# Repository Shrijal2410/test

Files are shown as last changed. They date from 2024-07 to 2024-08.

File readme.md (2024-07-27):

# Bionic Arm

Our project aims to provide a realistic, functional prosthetic hand for those who have lost theirs. We're not delving into mastering neurology; instead, we're focusing on using muscle sensor data (EMG) to control the hand's movements. Our design is intended for individuals with sufficient remaining limb functionality to provide us with EMG signals, allowing us to move the fingers and wrist accordingly.

## Objectives

Simple enough to outline, but challenging to achieve:

- Create a functional hand with full control over five fingers and wrist movement.
- Ensure the hand can carry up to 1-2kg and grip objects easily.
- Keep the overall weight under 500g, which is a challenge compared to some existing industrial designs.

## Folder Structure

I’ve kept a minimal yet comprehensive folder structure. Ensure each folder has a `README.md`. No spaces in file names use hyphens '-' or underscores '_'. Keep all file and folder names in lowercase. Stick to this template, but feel free to make necessary adjustments.

```
📁 bionicarm
│
├── 🗃️ code
│   └── 🗂️ esp32
│       ├── 🗂️ build
│       │   ├── 🗂️ multipleMotor
│       │   ├── 🗂️ multipleMotorWithGUI
│       │   └── 🗂️ singleMotor
│       └── 🗂️ test
│           ├── 🗂️ pid
│           └── 🗂️ sensorData
│   └── 🗂️ matlab
│
├── 🗃️ data
│   └── 🗂️ raw
│
├── 🗃️ docs
│   └── 🗂️ research
│
├── 🗃️ electrical
│   ├── 🗂️ assets
│   │   ├── 🗂️ 3dmodel
│   │   ├── 🗂️ footprint
│   │   └── 🗂️ symbol
│   ├── 🗂️ production
│   └── 🗂️ schematic
│
└── 🗃️ mechanical
    └── 🗂️ stl
```

## Commit Message Guidelines

Keep commit messages clean and meaningful. Use the following structure and ensure messages are in lowercase:

```
<type>(<scope>): <short summary>
│       │             │
│       │             └─⫸ Summary in present tense. Not capitalized. No period at the end.
│       │                  - use bullet points for clarity
│       │
│       └─⫸ Commit Scope: mechanical|electrical|firmware|software|integration|documentation
│
└─⫸ Commit Type: build|ci|docs|feat|fix|perf|refactor|test
```

### Example

```
feat(firmware-control): add PID controller for motor speed regulation

- enhances motor speed accuracy
- improves response time
```

### Important Note

Stick to this format to avoid the need for commit message modification via `git rebase`, which could inadvertently list me as a contributor to your commit. This ensures proper credit for your work.

## License

Not my area of expertise. So, I’m leaving this part to someone else.

**Note:** The goal of this README is to provide an overview of the project and guide users on where to go. Keep its purpose in mind while updating.

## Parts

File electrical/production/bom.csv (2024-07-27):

Designator | Footprint | Quantity | Value | LCSC Part #
C1, C2, C3 | CP_Radial_D4.0mm_P2.00mm | 3 | C_Small
D1 | D_DO-35_SOD27_P7.62mm_Horizontal | 1 | D_Small
D2, D3 | LED_D5.0mm_Horizontal_O1.27mm_Z3.0mm | 2 | LED_Small
D4 | LED_D5.0mm-4_RGB | 1 | LED_RGBA
F1 | RGEF500 | 1 | Polyfuse_Small
J1 | TerminalBlock_Phoenix_MKDS-1,5-4-5.08_1x04_P5.08mm_Horizontal | 1 | Screw_Terminal_01x04
M1, M2, M3, M4, M5, M6, M7 | JST_1x06_P2.54mm_Vertical | 7 | N20
MD1, MD2, MD3, MD4 | TB6612 | 4 | TB6612
R1, R2, R3, R4 | R_Axial_DIN0207_L6.3mm_D2.5mm_P7.62mm_Horizontal | 4 | R_Small
RV1 | Potentiometer_Runtron_RM-065_Vertical | 1 | R_Potentiometer_Small
S1, S2 | JST_1x03_P2.54mm_Vertical | 2 | EMG2
T1 | TestPoint_Pad_1.0x1.0mm | 1 | TestPoint_Probe
U1 | ESP32 | 1 | ESP32
U2 | SAMD09 | 1 | SAMD09
U3, U4 | CD4069 | 2 | CD4069
U5 | PinHeader_1x03_P2.54mm_Vertical | 1 | LM338

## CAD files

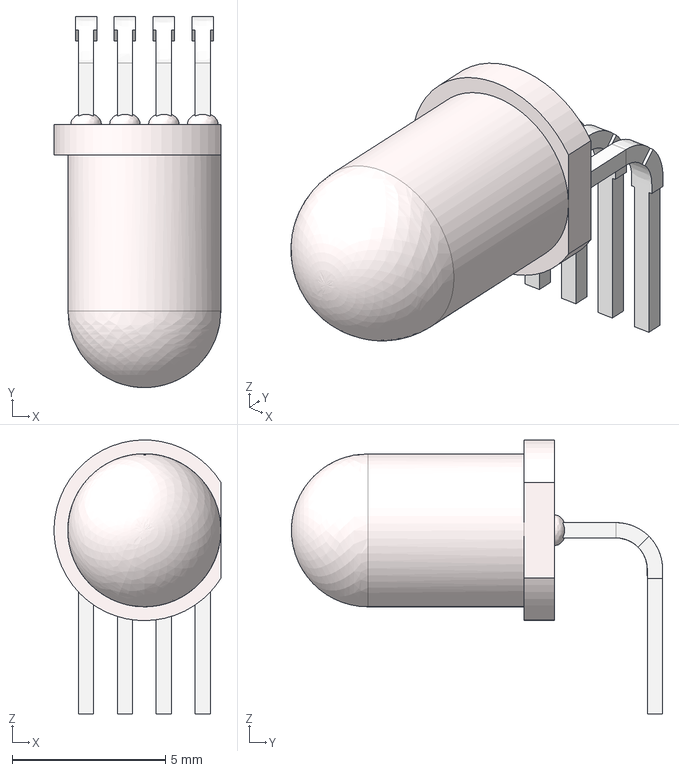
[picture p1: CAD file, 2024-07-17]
electrical/assets/3dmodel/LED_RGB_H1mm.stp
5.45 x 12.1 x 8.95 mm

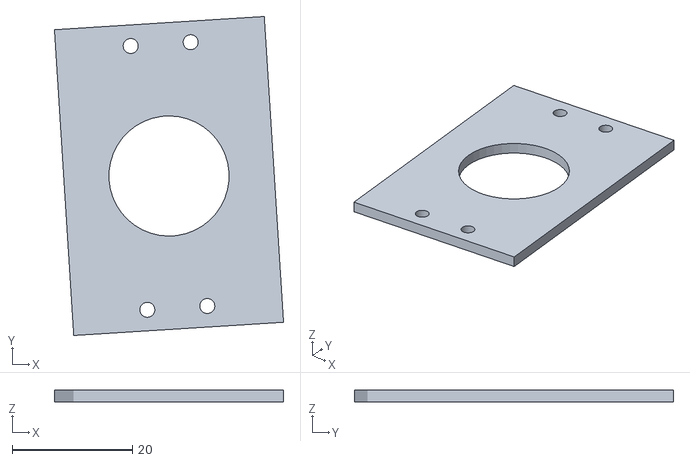
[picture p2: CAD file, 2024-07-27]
mechanical/stl/forearm/Assem2 - Part21-1.STL
38.1 x 53.1 x 2.00

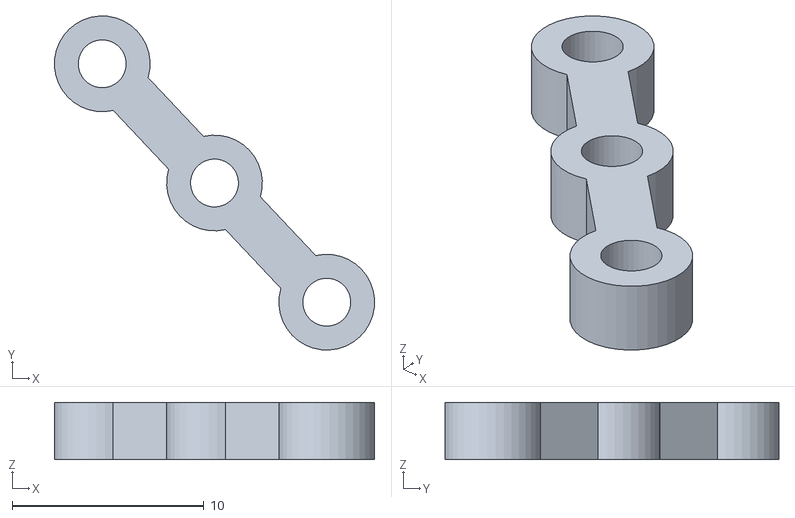
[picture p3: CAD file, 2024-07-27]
mechanical/stl/plam/Assem3 - Part4_middle-1.STL
16.7 x 17.4 x 3.00

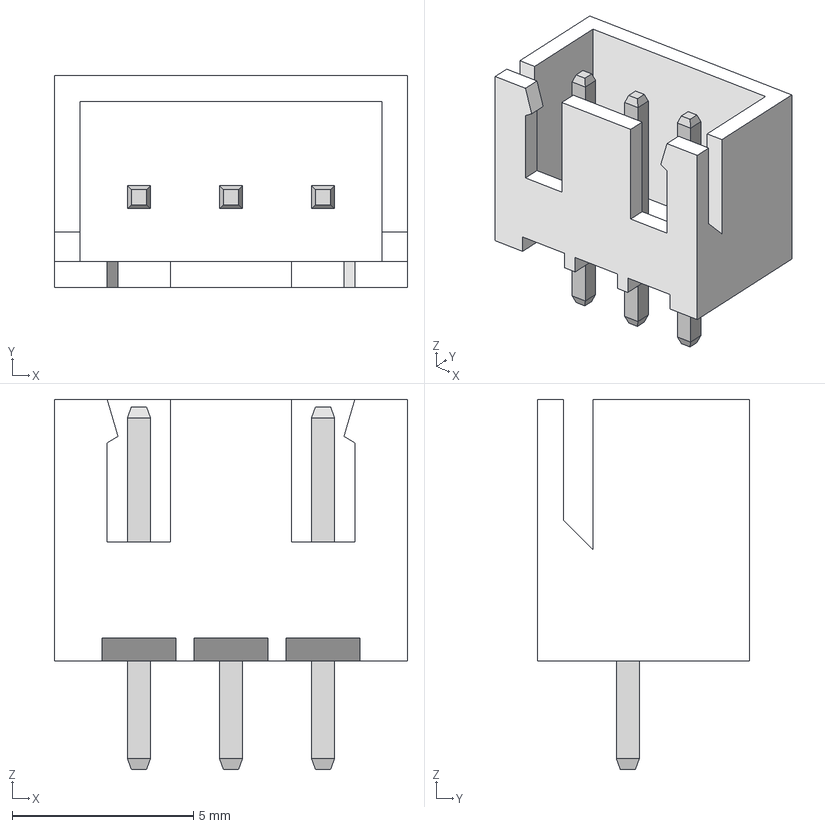
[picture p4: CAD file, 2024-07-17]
electrical/assets/3dmodel/JST_XH_1x03_P2.54mm_Vertical.step
9.75 x 5.84 x 10.2 mm

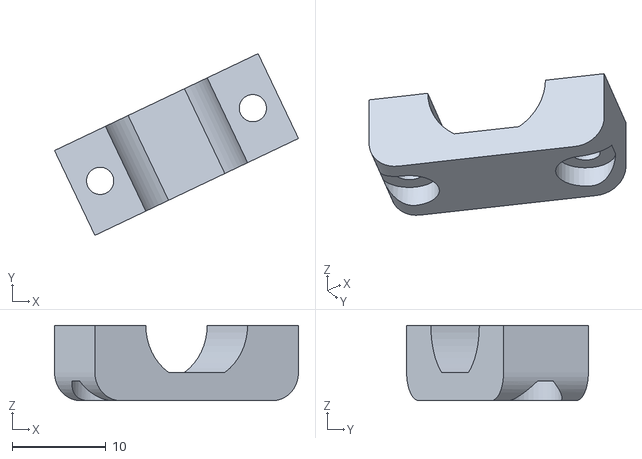
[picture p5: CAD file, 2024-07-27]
mechanical/stl/forearm/Assem2 - Part19-2.STL
26.0 x 19.3 x 8.00

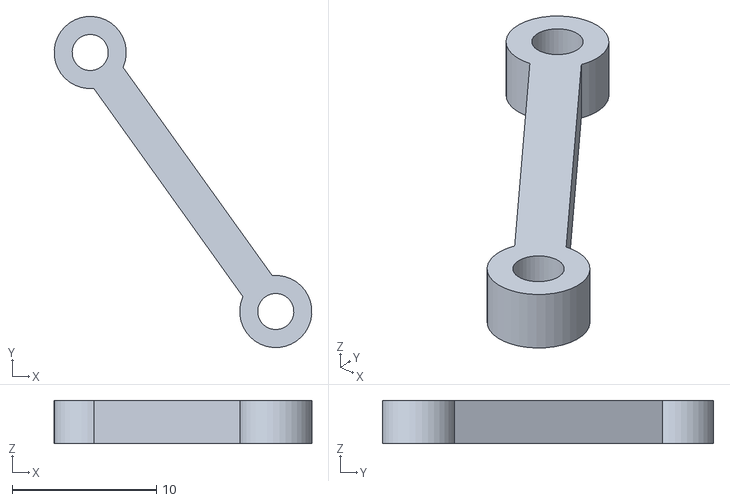
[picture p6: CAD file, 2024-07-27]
mechanical/stl/plam/Assem3 - Part5_little-1.STL
17.8 x 22.9 x 3.00

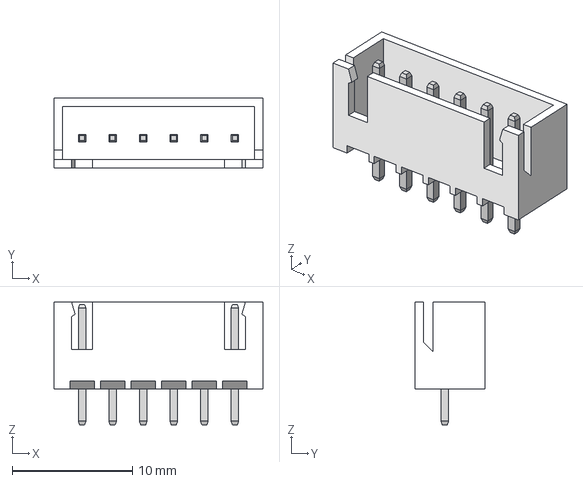
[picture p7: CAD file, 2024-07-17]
electrical/assets/3dmodel/JST_XH_1x06_P2.54mm_Vertical.stp
17.4 x 5.84 x 10.2 mm

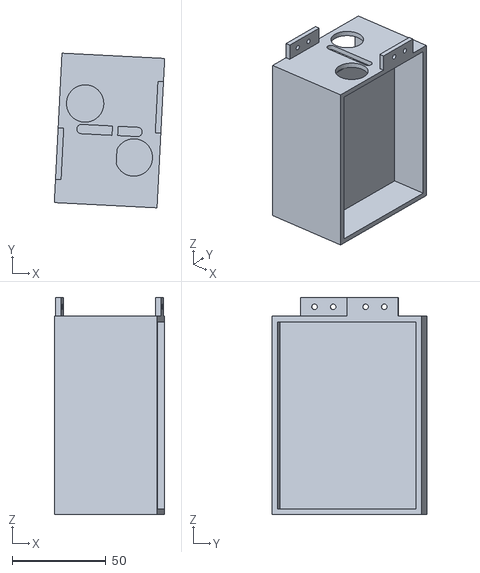
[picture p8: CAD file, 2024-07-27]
mechanical/stl/forearm/Assem2 - Part23-1.STL
59.0 x 82.7 x 116.0

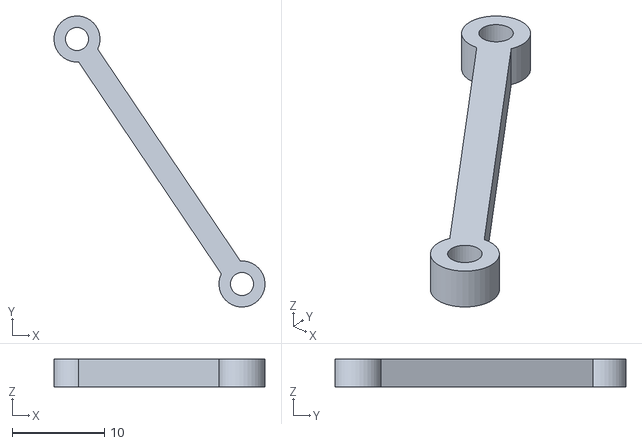
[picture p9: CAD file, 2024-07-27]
mechanical/stl/plam/Assem3 - Part5_thumb-1.STL
22.9 x 31.6 x 3.00

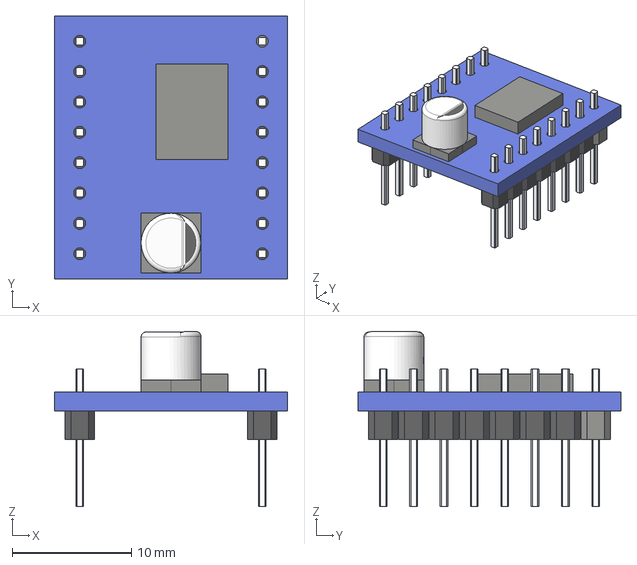
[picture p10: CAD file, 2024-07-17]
electrical/assets/3dmodel/TB6612.step
19.5 x 22.0 x 14.7 mm

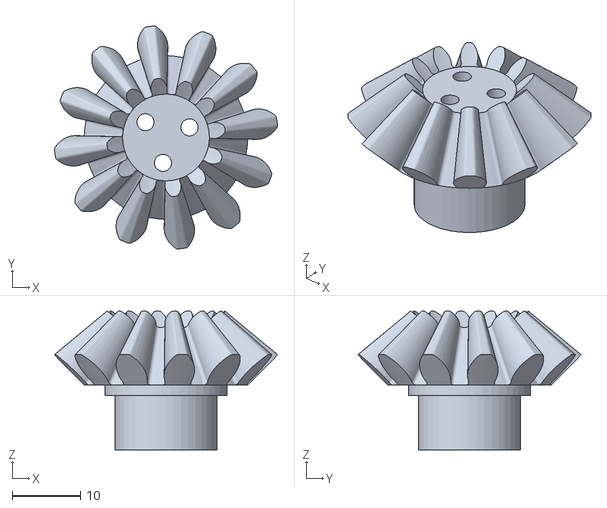
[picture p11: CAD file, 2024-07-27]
mechanical/stl/forearm/Assem2 - Bevel Gear3-3.STL
32.7 x 32.7 x 20.3

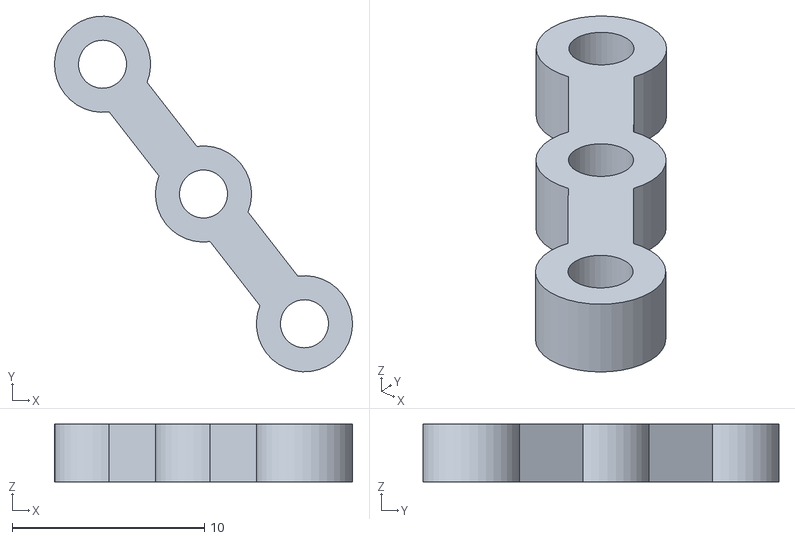
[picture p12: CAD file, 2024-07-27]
mechanical/stl/plam/Assem3 - Part4_little-1.STL
15.5 x 18.5 x 3.00

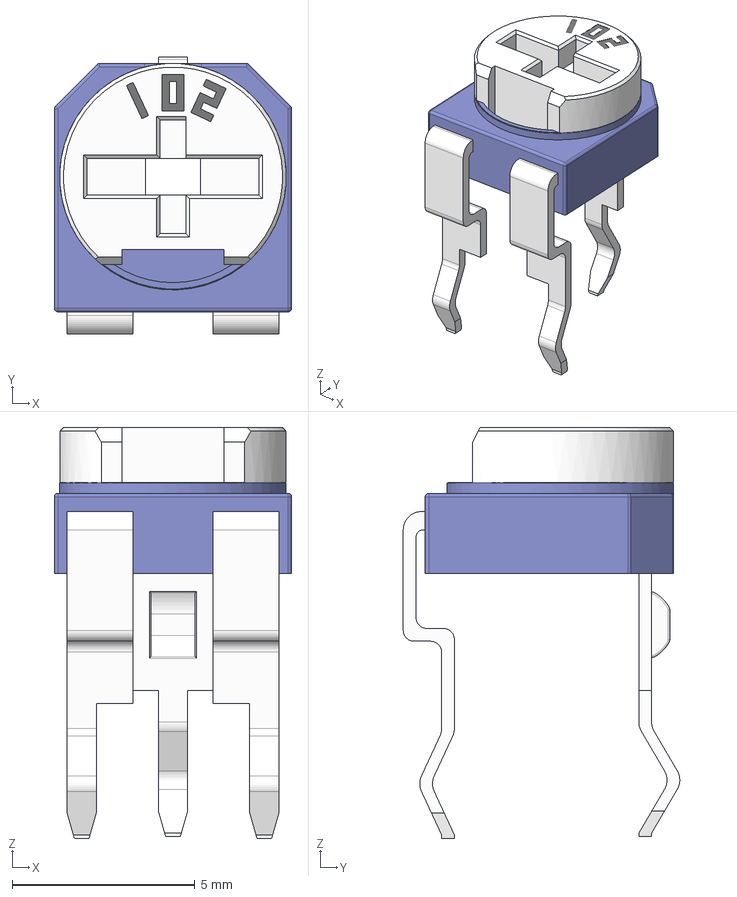
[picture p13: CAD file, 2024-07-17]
electrical/assets/3dmodel/POT_Trim.step
6.50 x 7.57 x 11.2 mm

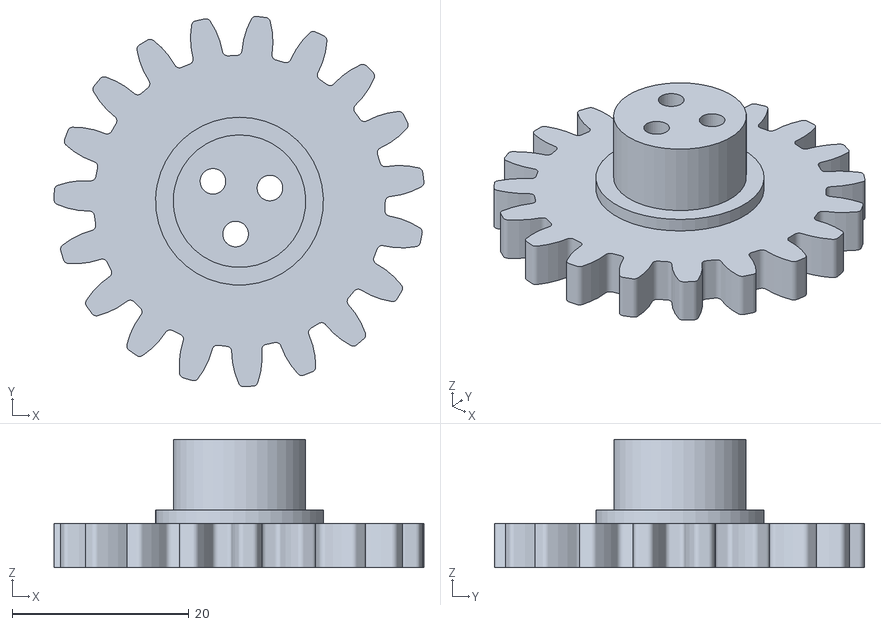
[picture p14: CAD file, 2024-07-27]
mechanical/stl/forearm/Assem2 - gear 40 teeth-2.STL
41.9 x 41.9 x 14.5

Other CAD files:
mechanical/stl/plam/Assem3 - Part11-2.STL
mechanical/stl/forearm/Assem2 - Part29-1.STL
mechanical/stl/plam/Assem3 - Part4_thumb-1.STL
electrical/assets/3dmodel/CD4069.step
electrical/assets/3dmodel/RGEF500.stp
electrical/assets/3dmodel/SAMD09.step
mechanical/stl/forearm/Assem2 - Bevel Gear3-1.STL
mechanical/stl/forearm/Assem2 - Bevel Gear3-4.STL
mechanical/stl/forearm/Assem2 - Part17-1.STL
mechanical/stl/forearm/Assem2 - Part17-2.STL
mechanical/stl/forearm/Assem2 - Part18-1.STL
mechanical/stl/forearm/Assem2 - Part19-1.STL
mechanical/stl/forearm/Assem2 - Part20_1-1.STL
mechanical/stl/forearm/Assem2 - Part20_1-2.STL
mechanical/stl/forearm/Assem2 - Part20_2-1.STL
mechanical/stl/forearm/Assem2 - Part22-1.STL
mechanical/stl/forearm/Assem2 - Part30-1.STL
mechanical/stl/forearm/Assem2 - Part30-2.STL
mechanical/stl/forearm/Assem2 - gear 10-1.STL
mechanical/stl/forearm/Assem2 - gear 10-2.STL
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

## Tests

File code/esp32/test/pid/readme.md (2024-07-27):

# PID Controller

## Procedure

### Part 1: Reading from the Encoder

### Part 2: Measure position

### Part 3: Drive the motor

### Part 4: Control the motor

## Tutorial

https://curiores.com/positioncontrol

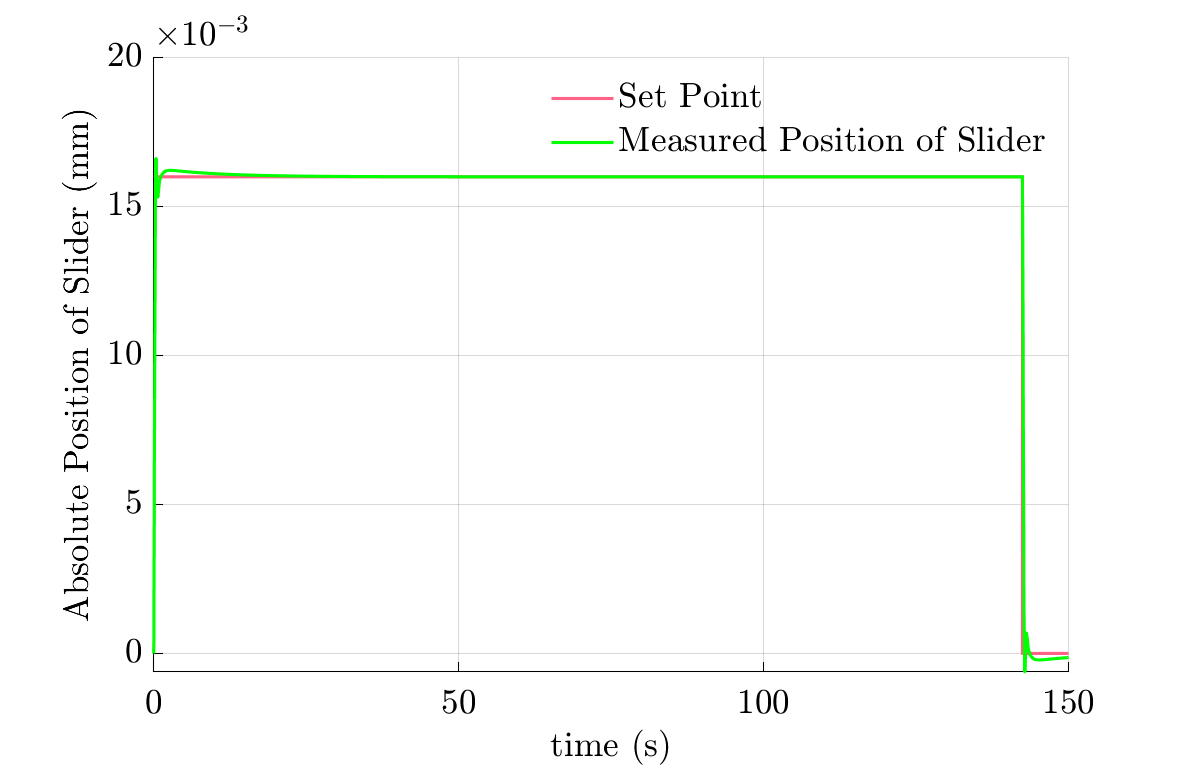
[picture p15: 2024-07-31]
Simulation Results/Index_finger_png_figure.png

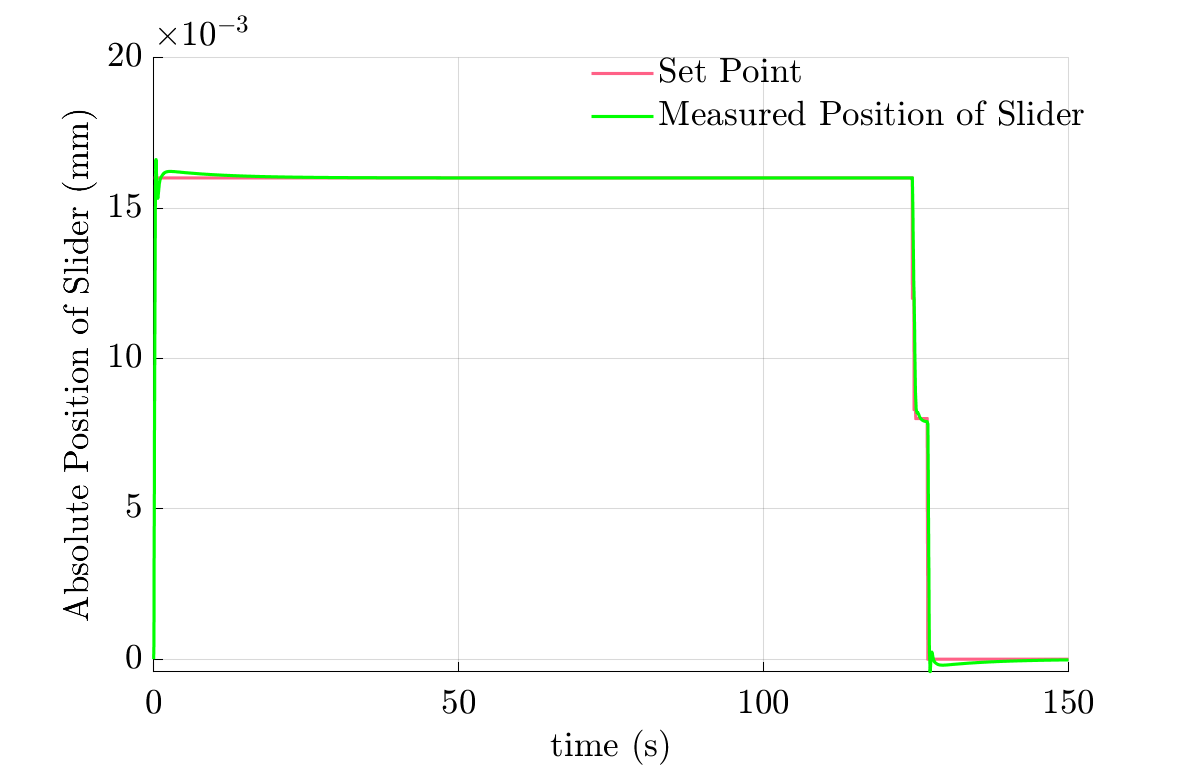
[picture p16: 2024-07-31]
Simulation Results/Ring_finger_png_figure.png

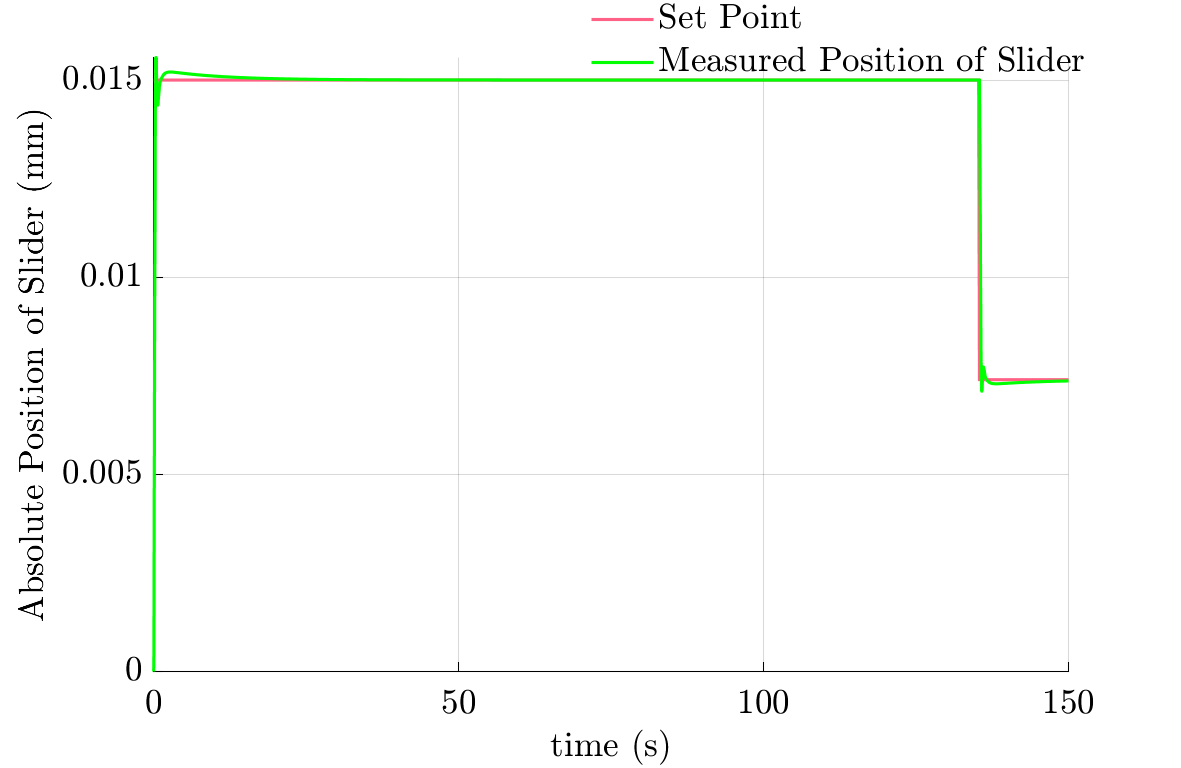
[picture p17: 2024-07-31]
Simulation Results/Middle_finger_png_figure.png

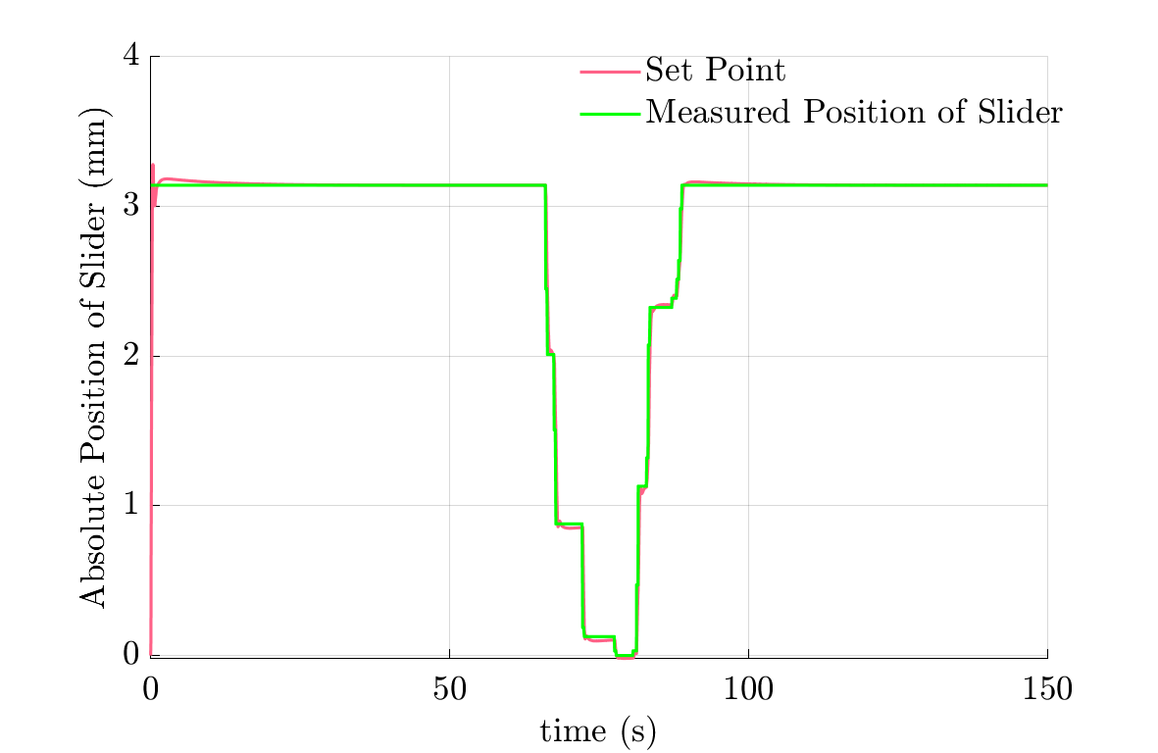
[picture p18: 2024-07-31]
Simulation Results/Wrist_roll_png_figure.png

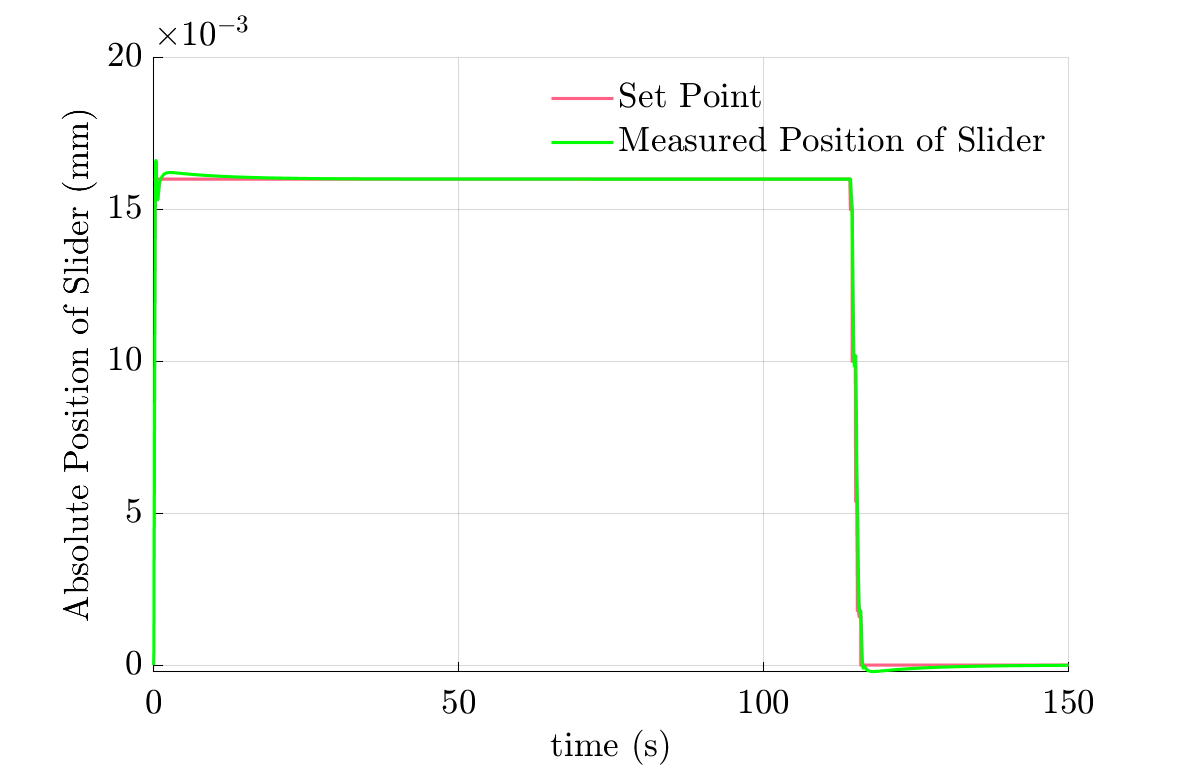
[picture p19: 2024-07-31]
Simulation Results/Little_finger_png_figure.png

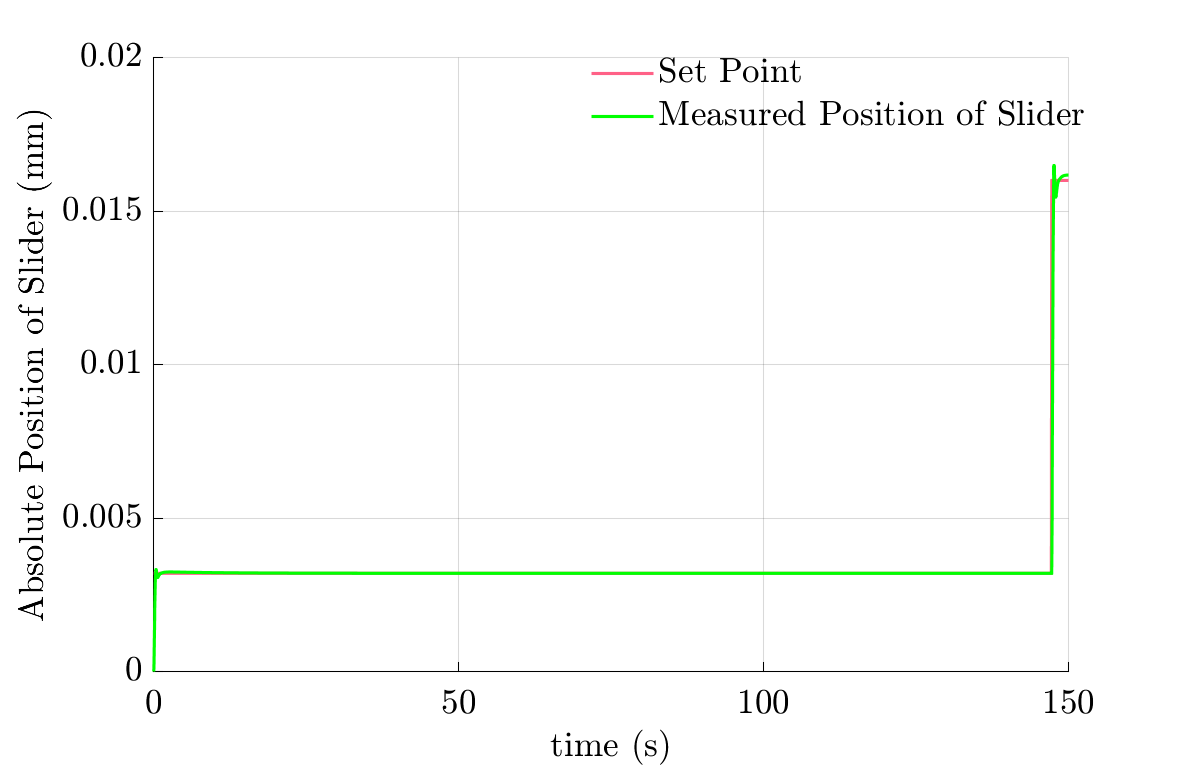
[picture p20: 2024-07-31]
Simulation Results/Thumb_png_figure.png

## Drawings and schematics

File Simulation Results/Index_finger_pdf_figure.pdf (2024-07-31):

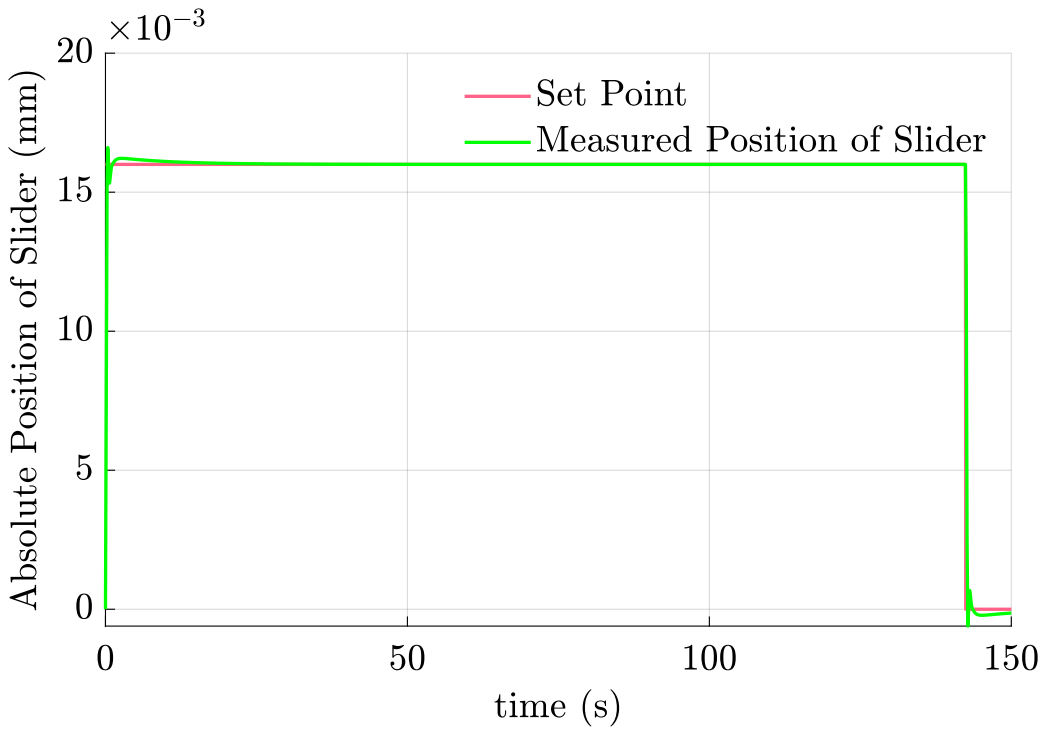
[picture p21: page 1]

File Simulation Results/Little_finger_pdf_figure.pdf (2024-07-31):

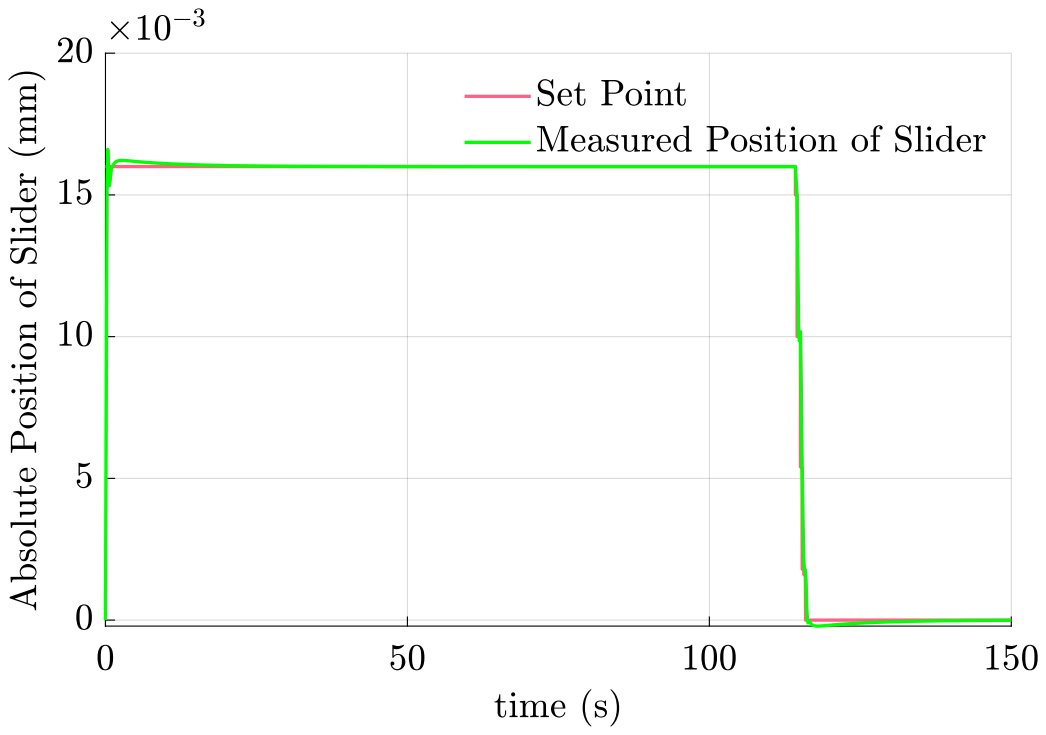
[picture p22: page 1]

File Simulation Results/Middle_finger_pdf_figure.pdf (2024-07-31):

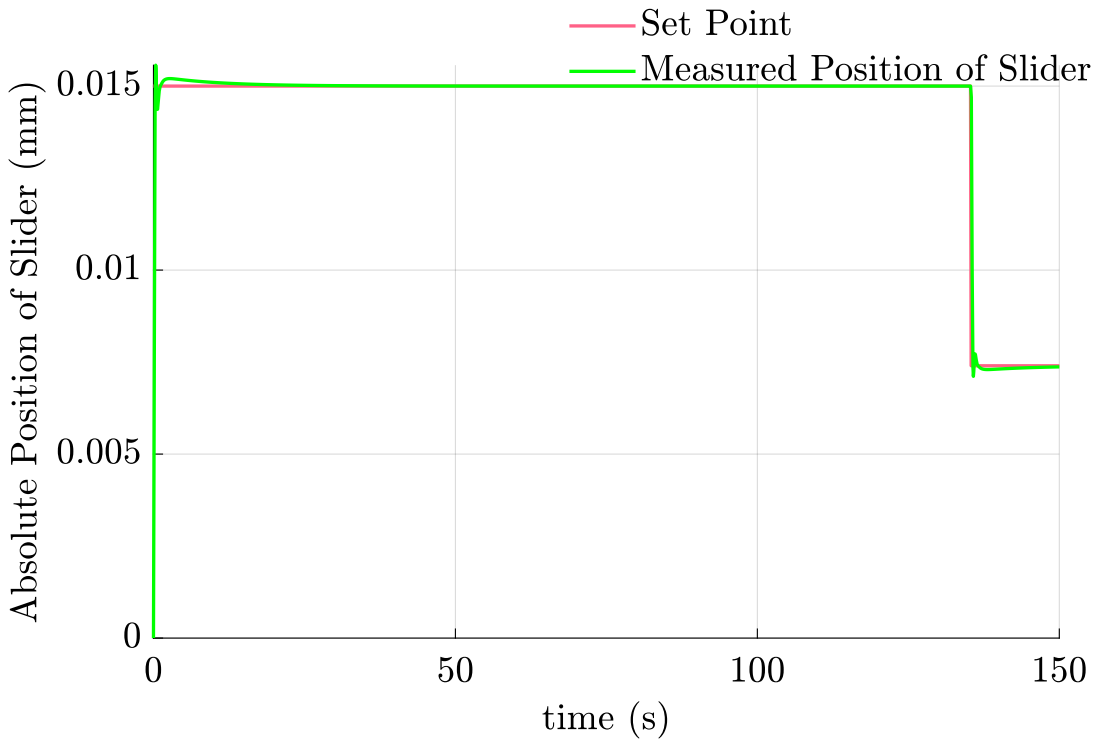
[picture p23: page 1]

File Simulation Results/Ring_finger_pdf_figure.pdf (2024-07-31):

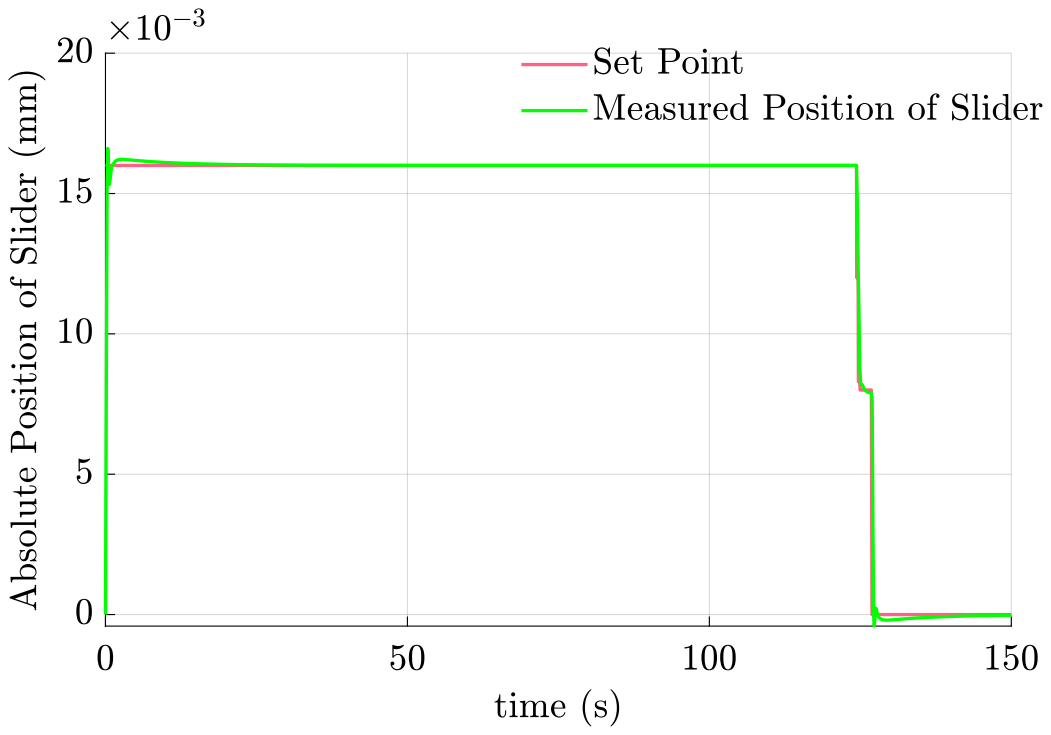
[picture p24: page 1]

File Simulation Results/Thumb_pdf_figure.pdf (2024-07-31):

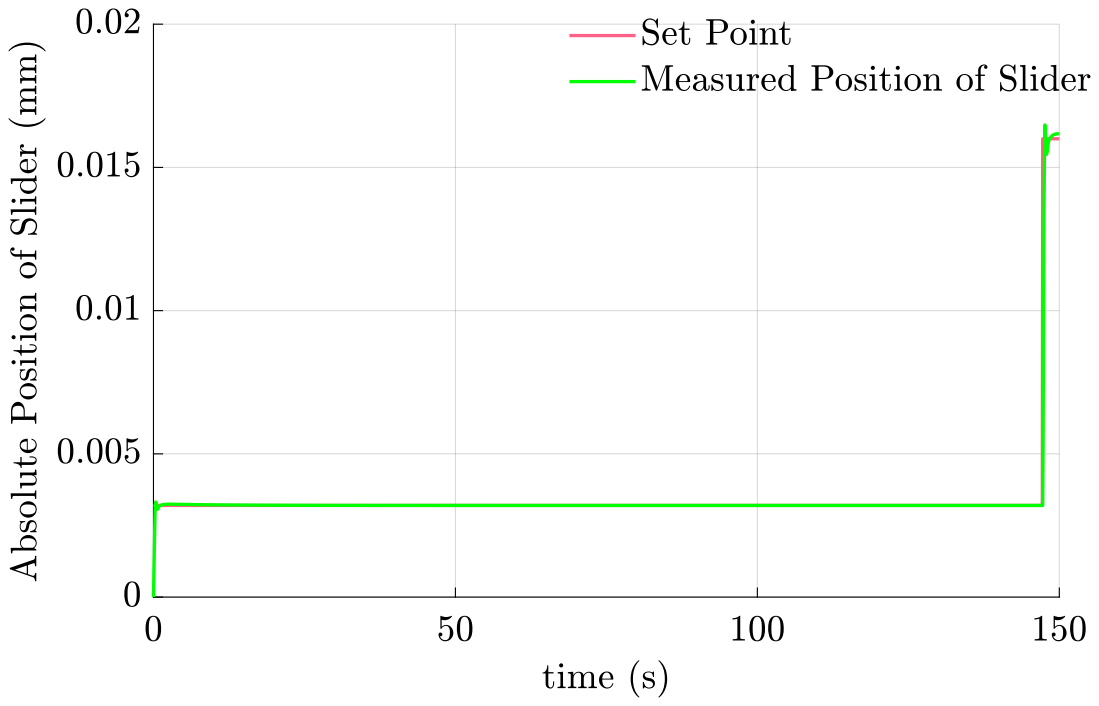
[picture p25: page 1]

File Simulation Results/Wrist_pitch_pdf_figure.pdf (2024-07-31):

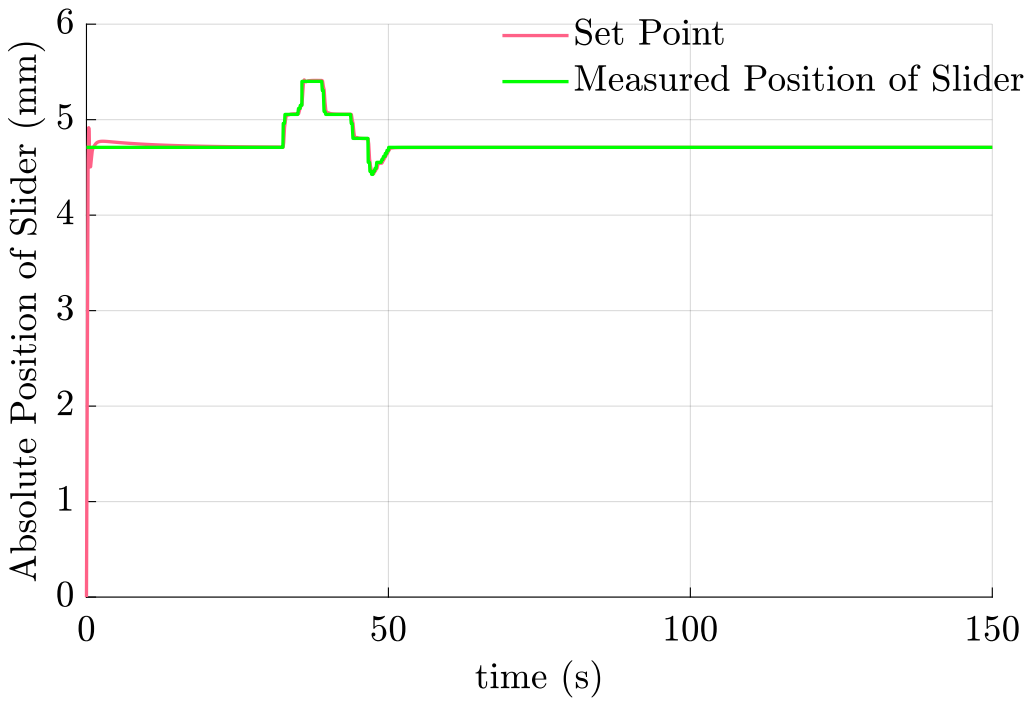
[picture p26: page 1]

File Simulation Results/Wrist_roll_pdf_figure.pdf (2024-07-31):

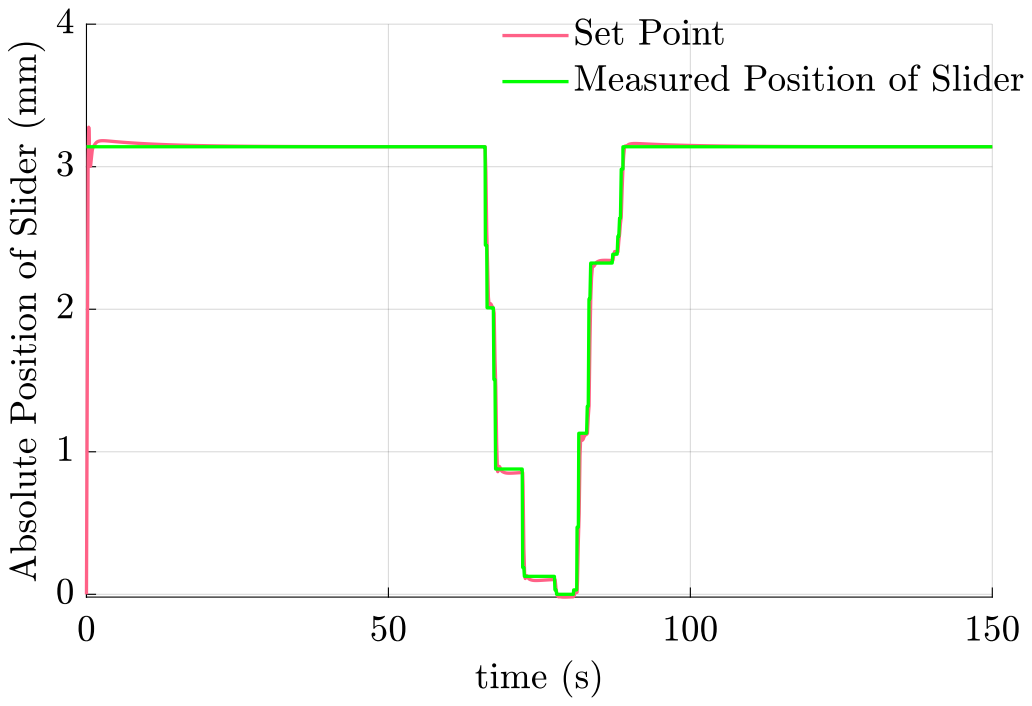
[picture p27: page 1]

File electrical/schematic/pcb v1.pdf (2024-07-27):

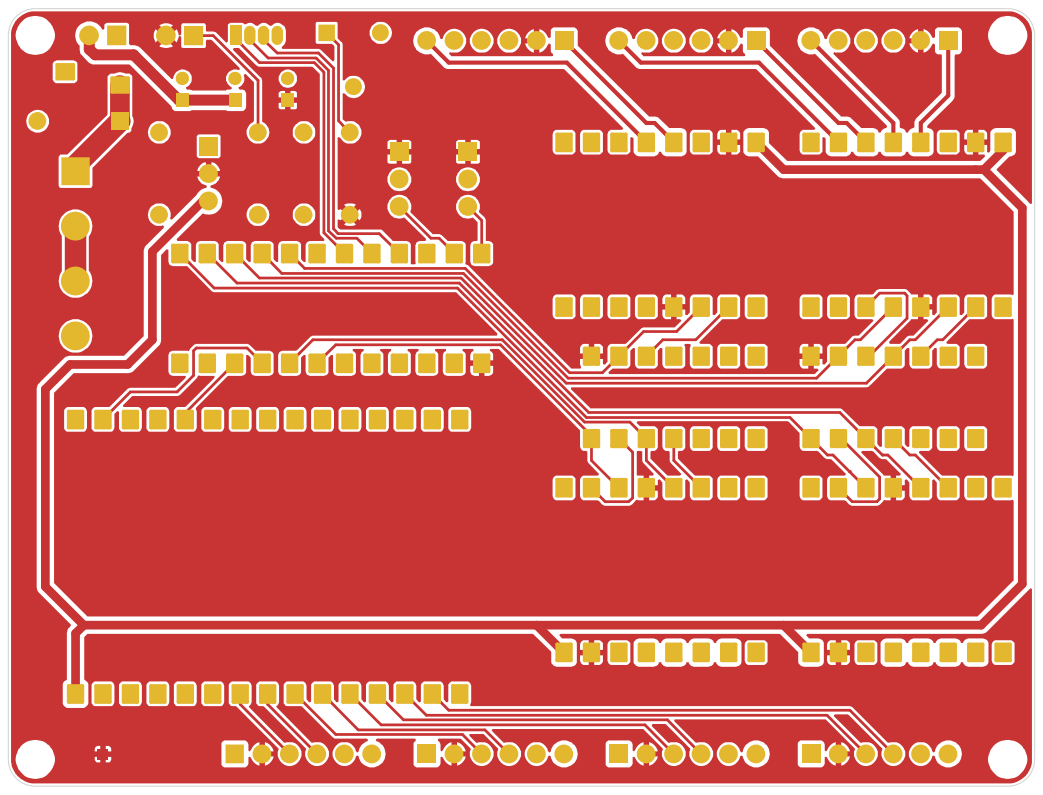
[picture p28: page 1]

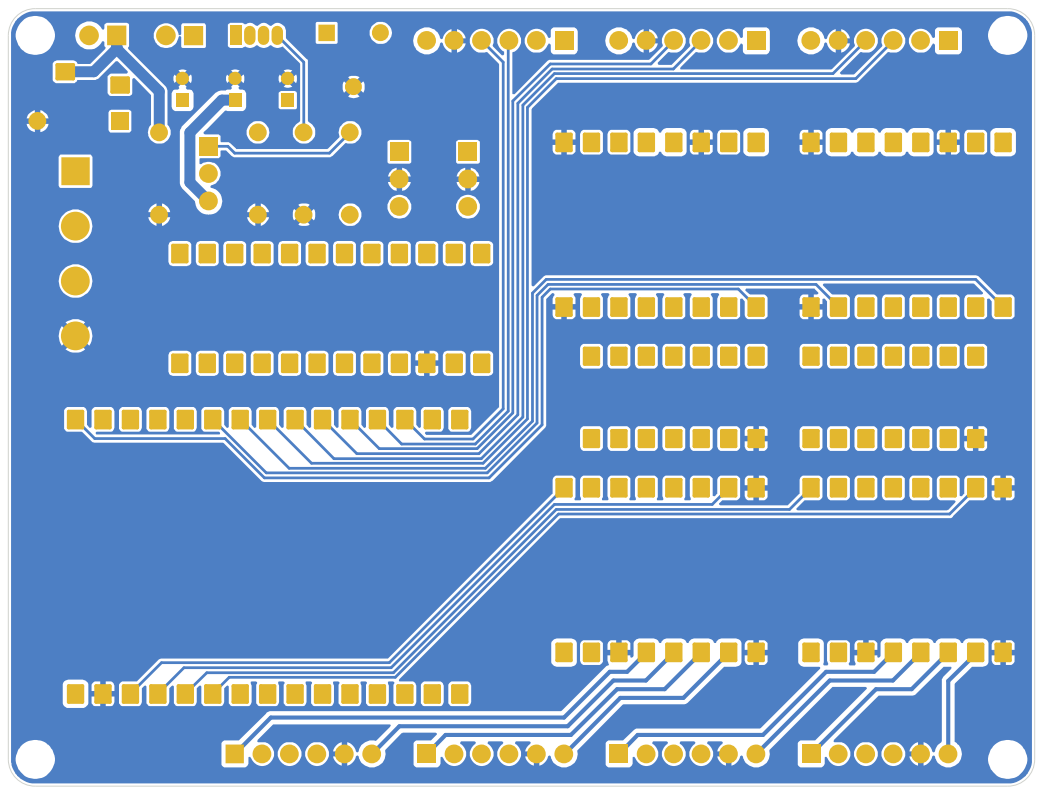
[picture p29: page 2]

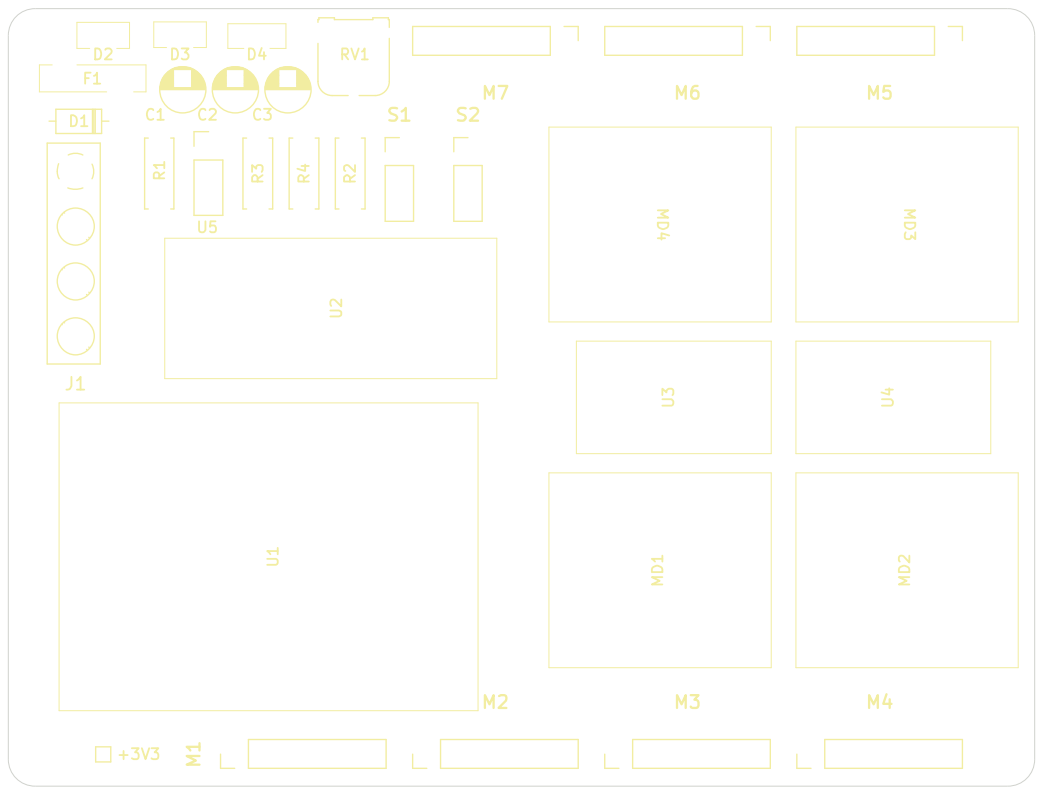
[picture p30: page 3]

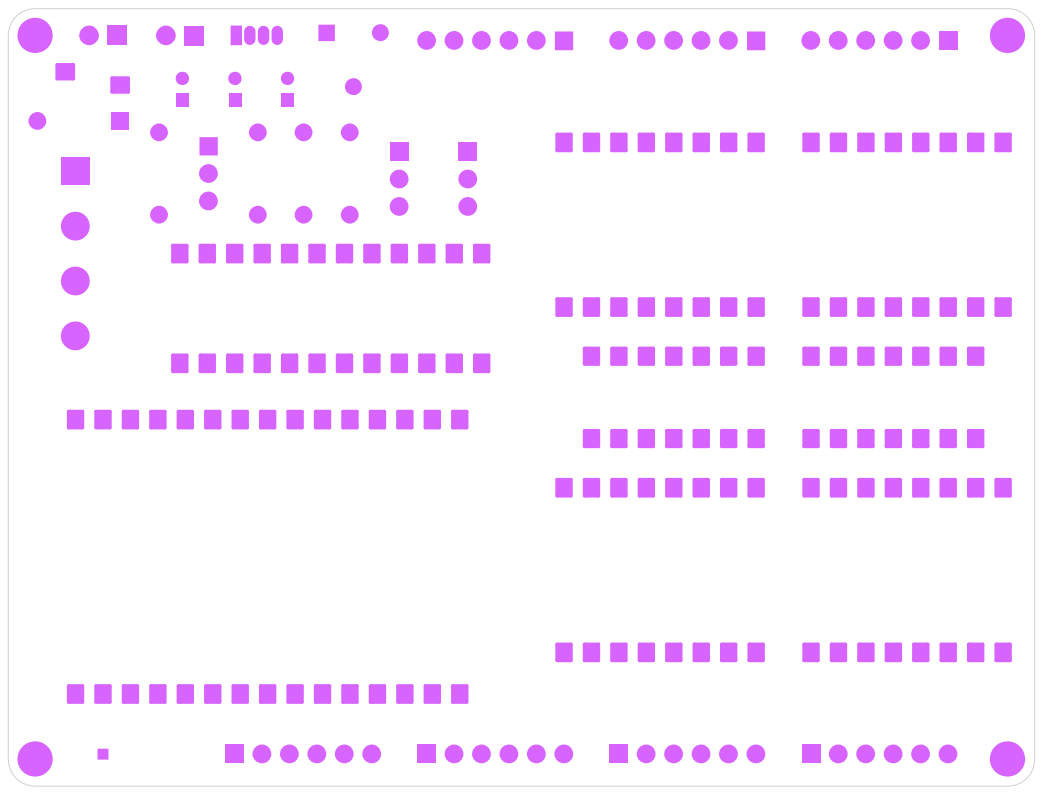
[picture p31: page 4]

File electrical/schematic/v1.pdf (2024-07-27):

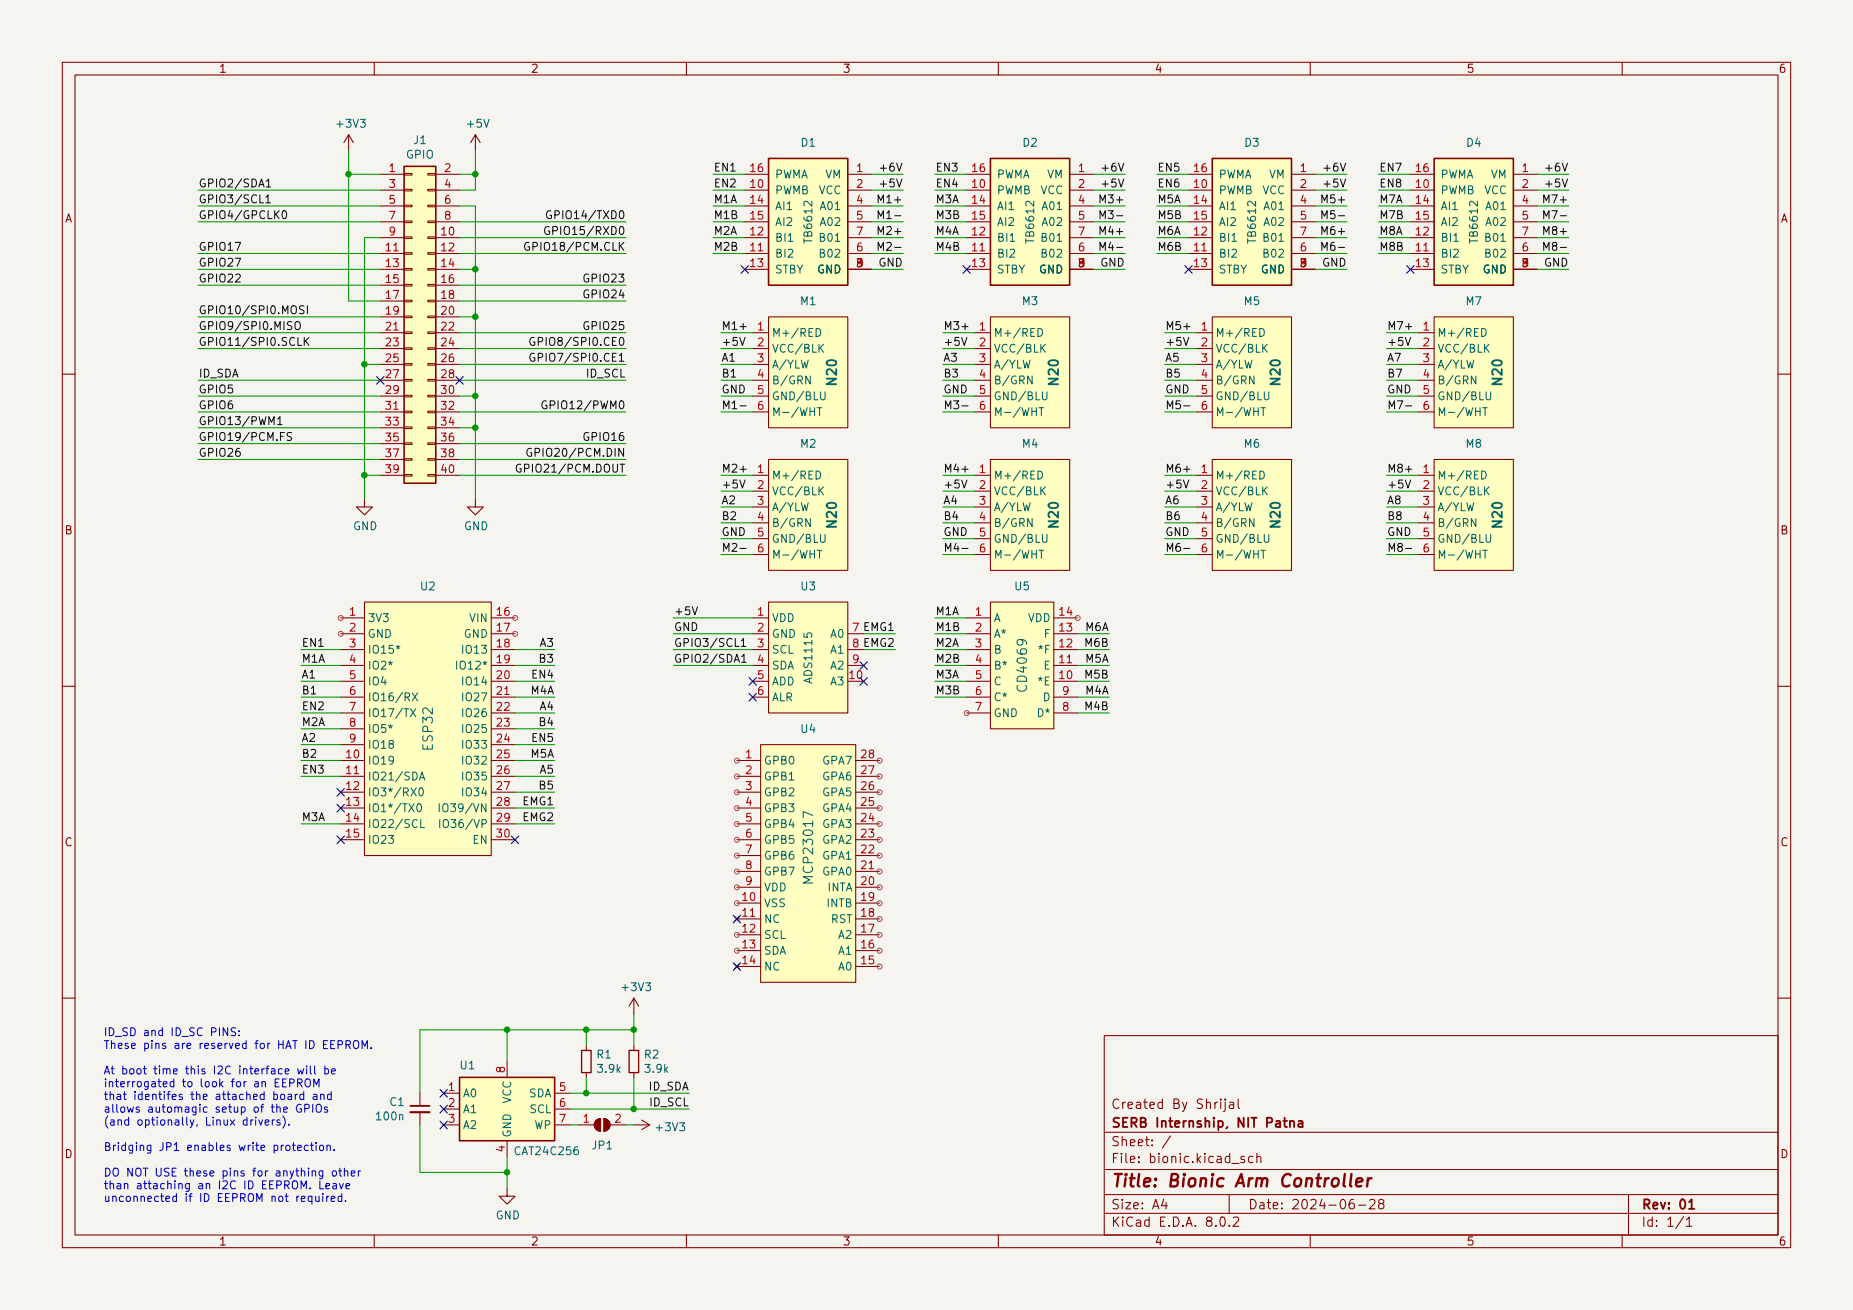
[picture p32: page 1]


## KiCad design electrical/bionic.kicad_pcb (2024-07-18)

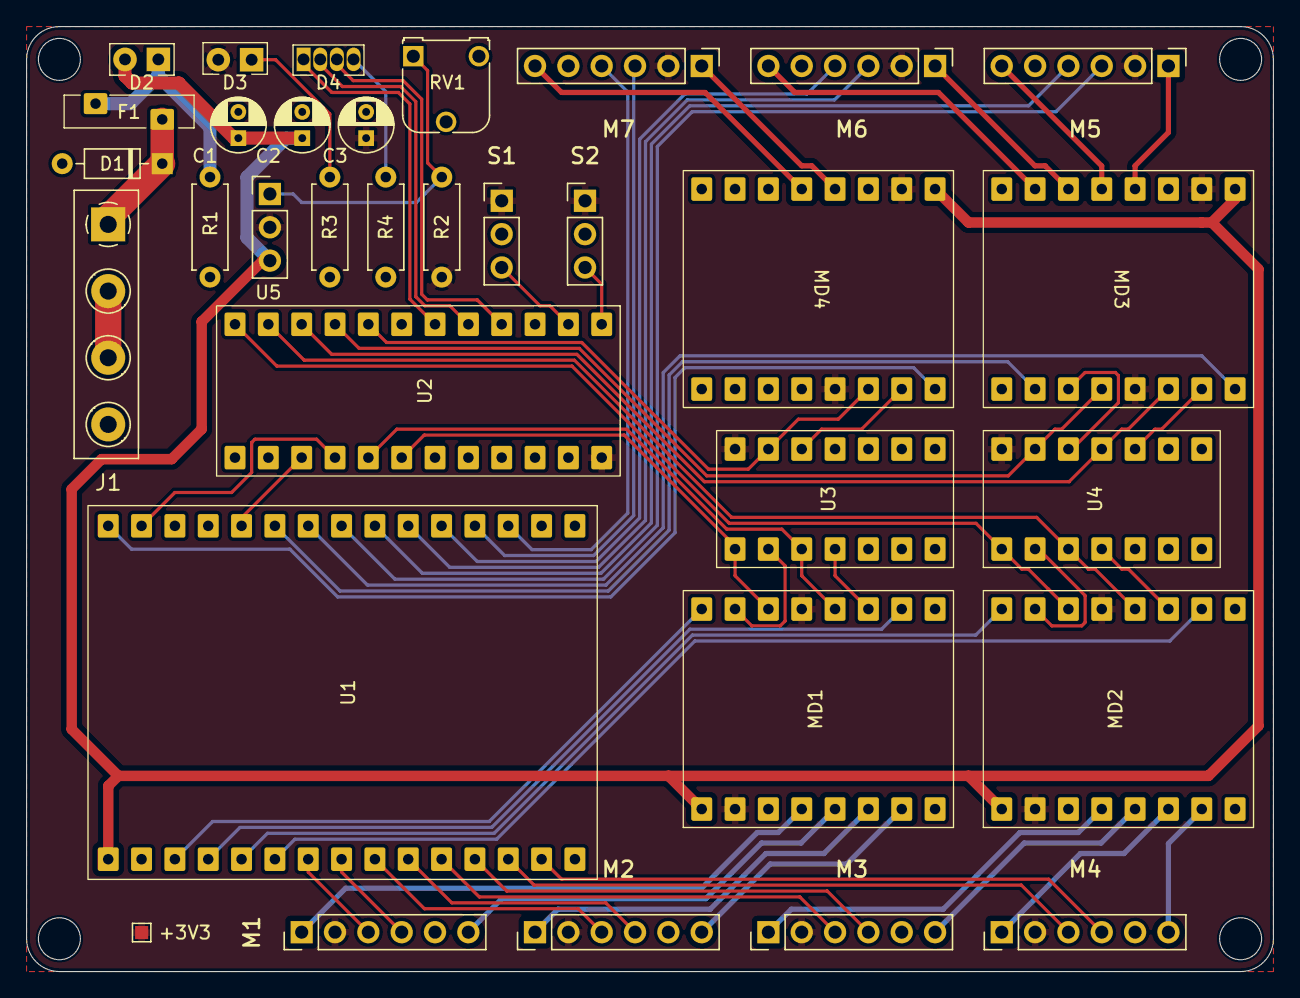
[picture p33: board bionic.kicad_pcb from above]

Board: 2 copper layers, 95.0 x 72.0 mm, 37 parts (0 on the bottom side), 65 nets.

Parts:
C1, C2, C3: C_Small; CP_Radial_D4.0mm_P2.00mm
D1: D_Small; D_DO-35_SOD27_P7.62mm_Horizontal
D2, D3: LED_Small; LED_D5.0mm_Horizontal_O1.27mm_Z3.0mm
D4: LED_RGBA; LED_D5.0mm-4_RGB
F1: Polyfuse_Small; RGEF500
H1, H2, H3, H4: MountingHole; MountingHole_3.2mm_M3
J1: Screw_Terminal_01x04; TerminalBlock_Phoenix_MKDS-1,5-4-5.08_1x04_P5.08mm_Horizont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
M1, M2, M3, M4, M5, M6, M7: N20; JST_1x06_P2.54mm_Vertical
MD1, MD2, MD3, MD4: TB6612
R1, R2, R3, R4: R_Small; R_Axial_DIN0207_L6.3mm_D2.5mm_P7.62mm_Horizontal
RV1: R_Potentiometer_Small; Potentiometer_Runtron_RM-065_Vertical
S1, S2: EMG2; JST_1x03_P2.54mm_Vertical
T1: TestPoint_Probe; TestPoint_Pad_1.0x1.0mm
U1: ESP32
U2: SAMD09
U3, U4: CD4069
U5: LM338; PinHeader_1x03_P2.54mm_Vertical

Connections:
/+3V3: C3.1, D3.2 (A), M1.2 (VCC/BLK), M2.2 (VCC/BLK), M3.2 (VCC/BLK), M4.2 (VCC/BLK), M5.2 (VCC/BLK), M6.2 (VCC/BLK), M7.2 (VCC/BLK), MD1.2 (VCC), MD1.13 (STBY), MD2.2 (VCC), MD2.13 (STBY), MD3.2 (VCC), MD3.13 (STBY), MD4.2 (VCC), MD4.13 (STBY), R2.1, S1.1 (VIN), S2.1 (VIN), T1.1, U2.24 (VIN), U3.14 (VDD), U4.14 (VDD), U5.2 (OUT)
/+6V: C1.1, C2.1, D2.2 (A), MD1.1 (VM), MD2.1 (VM), MD3.1 (VM), MD4.1 (VM), U1.16 (VIN), U5.3 (IN)
/DIR1: MD1.14 (AI1), U2.18 (25), U3.1 (A)
/DIR2: MD1.12 (BI1), U2.17 (24), U3.3 (B)
/DIR3: MD2.14 (AI1), U2.12 (15), U4.1 (A)
/DIR4: MD2.12 (BI1), U2.11 (14), U4.3 (B)
/DIR5: MD3.14 (AI1), U2.10 (11), U4.11 (E)
/DIR6: MD3.12 (BI1), U2.9 (10), U4.13 (F)
/DIR7: MD4.14 (AI1), U2.8 (9), U3.13 (F)
/EMG1: S1.3 (ENV), U2.2 (*3)
/EMG2: S2.3 (ENV), U2.1 (*2)
/ENA1: M1.3 (A/YLW), U1.22 (IO26)
/ENA2: M2.3 (A/YLW), U1.24 (IO33)
/ENA3: M3.3 (A/YLW), U1.26 (IO35)
/ENA4: M4.3 (A/YLW), U1.28 (IO39/VN)
/ENA5: M5.3 (A/YLW), U1.8 (IO5*)
/ENA6: M6.3 (A/YLW), U1.6 (IO16/RX)
/ENA7: M7.3 (A/YLW), U1.4 (IO2*)
/ENB1: M1.4 (B/GRN), U1.23 (IO25)
/ENB2: M2.4 (B/GRN), U1.25 (IO32)
/ENB3: M3.4 (B/GRN), U1.27 (IO34)
/ENB4: M4.4 (B/GRN), U1.29 (IO36/VP)
/ENB5: M5.4 (B/GRN), U1.7 (IO17/TX)
/ENB6: M6.4 (B/GRN), U1.5 (IO4)
/ENB7: M7.4 (B/GRN), U1.3 (IO15*)
/L_BLU: D4.3 (BK), U2.4 (~5)
/L_GRN: D4.2 (GK), U2.5 (~6)
/L_RED: D4.1 (RK), U2.6 (~7)
/M1+: M1.1 (M+/RED), MD1.4 (A01)
/M1-: M1.6 (M-/WHT), MD1.5 (A02)
/M1B: MD1.15 (AI2), U3.2 (A*)
/M2+: M2.1 (M+/RED), MD1.6 (B01)
/M2-: M2.6 (M-/WHT), MD1.7 (B02)
/M2B: MD1.11 (BI2), U3.4 (B*)
/M3+: M3.1 (M+/RED), MD2.4 (A01)
/M3-: M3.6 (M-/WHT), MD2.5 (A02)
/M3B: MD2.15 (AI2), U4.2 (A*)
/M4+: M4.1 (M+/RED), MD2.6 (B01)
/M4-: M4.6 (M-/WHT), MD2.7 (B02)
/M4B: MD2.11 (BI2), U4.4 (B*)
/M5+: M5.1 (M+/RED), MD3.4 (A01)
/M5-: M5.6 (M-/WHT), MD3.5 (A02)
/M5B: MD3.15 (AI2), U4.10 (*E)
/M6+: M6.1 (M+/RED), MD3.6 (B01)
/M6-: M6.6 (M-/WHT), MD3.7 (B02)
/M6B: MD3.11 (BI2), U4.12 (*F)
/M7+: M7.1 (M+/RED), MD4.4 (A01)
/M7-: M7.6 (M-/WHT), MD4.5 (A02)
/M7B: MD4.15 (AI2), U3.12 (*F)
/PWM1: MD1.16 (PWMA), U1.18 (IO13)
/PWM2: MD1.10 (PWMB), U1.19 (IO12*)
/PWM3: MD2.16 (PWMA), U1.20 (IO14)
/PWM4: MD2.10 (PWMB), U1.21 (IO27)
/PWM5: MD3.16 (PWMA), U1.9 (IO18)
/PWM6: MD3.10 (PWMB), U1.10 (IO19)
/PWM7: MD4.16 (PWMA), U1.15 (IO23)
/SCL: U1.14 (IO22/SCL), U2.16 (SCL)
/SDA: U1.11 (IO21/SDA), U2.15 (SDA)
GND: C1.2, C2.2, C3.2, D1.2 (A), J1.4, M1.5 (GND/BLU), M2.5 (GND/BLU), M3.5 (GND/BLU), M4.5 (GND/BLU), M5.5 (GND/BLU), M6.5 (GND/BLU), M7.5 (GND/BLU), MD1.3 (GND), MD1.8 (GND), MD1.9 (GND), MD2.3 (GND), MD2.8 (GND), MD2.9 (GND), MD3.3 (GND), MD3.8 (GND), MD3.9 (GND), MD4.3 (GND), MD4.8 (GND), MD4.9 (GND), R1.2, R3.2, R4.1, RV1.2, S1.2 (GND), S2.2 (GND), U1.17 (GND), U2.22 (GND), U3.7 (GND), U4.7 (GND)
unnamed: D1.1 (K), F1.1, J1.1
unnamed: D2.1 (K), F1.2, R1.1
unnamed: D3.1 (K), R3.1
unnamed: D4.4 (A), R4.2
unnamed: J1.2, J1.3
unnamed: R2.2, RV1.1, U5.1 (ADJ)

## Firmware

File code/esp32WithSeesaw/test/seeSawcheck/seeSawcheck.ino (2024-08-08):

/*
 * This example shows how to blink a pin on a seesaw.
 * Attach the positive (longer lead) of the LED to pin 15 on the seesaw, and
 * the negative lead of the LED to ground through a 1k ohm resistor.
 */

#include "Adafruit_seesaw.h"

Adafruit_seesaw ss;

#define BLINK_PIN1 15
#define BLINK_PIN2 11
#define PWM_PIN 5
#define ANA_PIN 2



void setup() {
  Serial.begin(115200);
  
  while (!Serial) delay(10);   // wait until serial port is opened
  
  if(!ss.begin()){
    Serial.println("seesaw not found!");
    while(1) delay(10);
  }
  
  Serial.println(F("seesaw started OK!"));

  ss.pinMode(BLINK_PIN1, OUTPUT);
  ss.pinMode(BLINK_PIN2, OUTPUT);
  ss.pinMode(PWM_PIN, OUTPUT);
  ss.pinMode(ANA_PIN, OUTPUT);

}

void loop() {
  ss.digitalWrite(BLINK_PIN1, HIGH); 
  ss.digitalWrite(BLINK_PIN2, HIGH); 
    // turn the LED on (HIGH is the voltage level)
  delay(100);                       // wait for a second
  ss.digitalWrite(BLINK_PIN1, LOW);
  ss.digitalWrite(BLINK_PIN2, LOW);    // turn the LED off by making the voltage LOW
      // turn the LED off by making the voltage LOW
  delay(100);  
  uint16_t pwmValue = 32768;  // 50% duty cycle for 16-bit PWM (range is 0 to 65535)
  
  // Write a 16-bit PWM value to the pin
  ss.analogWrite(PWM_PIN, pwmValue, 16);
  
  delay(2000);  // keep the LED at this brightness for 2 seconds

  pwmValue = 65535;  // 100% duty cycle for 16-bit PWM
  ss.analogWrite(PWM_PIN, pwmValue, 16);

  delay(2000);  // keep the LED at this brightness for 2 seconds

  pwmValue = 0;  // 0% duty cycle for 16-bit PWM (LED off)
  ss.analogWrite(PWM_PIN, pwmValue, 16);

  delay(2000);
  ss.digitalWrite(ANA_PIN, HIGH);
  delay(1000);
  ss.digitalWrite(ANA_PIN, LOW);
  delay(1000);
}

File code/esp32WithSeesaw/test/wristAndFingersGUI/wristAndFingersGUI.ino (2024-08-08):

#include "Adafruit_seesaw.h"
#include <WiFi.h>
#include <WebServer.h>

Adafruit_seesaw ss;

const char* ssid = "motog52";
const char* password = "12ka442ka1";

WebServer server(80);

class SimplePID
{
private:
    float kp, kd, ki, umax; // Parameters
    float eprev, eintegral; // Storage

public:
    // Constructor
    SimplePID() : kp(1), kd(0.1), ki(0.01), umax(255), eprev(0.0), eintegral(0.0) {}

    // A function to set the parameters
    void setParams(float kpIn, float kdIn, float kiIn, float umaxIn)
    {
        kp = kpIn;
        kd = kdIn;
        ki = kiIn;
        umax = umaxIn;
    }

    // A function to compute the control signal
    void evalu(int value, int target, float deltaT, int &pwr, int &dir)
    {
        // error
        int e = target - value;

        // derivative
        float dedt = (e - eprev) / (deltaT);

        // integral
        eintegral = eintegral + e * deltaT;

        // control signal
        float u = kp * e + kd * dedt + ki * eintegral;

        // motor power
        pwr = (int)fabs(u);
        if (pwr > umax)
        {
            pwr = umax;
        }

        // motor direction
        dir = 1;
        if (u < 0)
        {
            dir = -1;
        }

        // store previous error
        eprev = e;
    }
};

struct Motor {
  int pwm;
  int dir1;
  int dir2;
  bool isPwmSeesaw;
  bool isDualDir;
  bool reversed;
  int encA;
  int encB;
};

Motor motors[] = {
  {7, 24, -1, true, false, true, -1, -1},    // motor1 
  {6, 25, -1, true, false, true,-1,-1},   // motor2 
  {19, 10, -1, false, false, true,-1,-1},  // motor3 
  {23, 11, -1, false, false, true,-1,-1}, //motor 4
  {18, 14, -1, false, false, false, 16, 4},    // motor5 (reversed)
  {5, 9, -1, true, false, false, 5, 17},   //  motor6
};

const int motorCount = sizeof(motors) / sizeof(motors[0]);

long prevT = 0;
volatile int posi[] = {0, 0};
SimplePID pid[2];

// Target positions
int target[] = {0, 0};

void setup() {
  Serial.begin(115200);
  
  while (!Serial) delay(10);   // wait until serial port is opened
  
  if(!ss.begin()){
    Serial.println("seesaw not found!");
    while(1) delay(10);
  }
  
  Serial.println(F("seesaw started OK!"));

  // Set the pins as outputs for all motors
  for (int i = 0; i < motorCount; i++) {
    if (motors[i].isPwmSeesaw) {
      ss.pinMode(motors[i].pwm, OUTPUT);
    } else {
      pinMode(motors[i].pwm, OUTPUT);
    }
    ss.pinMode(motors[i].dir1, OUTPUT);
    if (motors[i].isDualDir) {
      ss.pinMode(motors[i].dir2, OUTPUT);
    }
  }

  for (int i = 4; i < motorCount; i++) {
    pinMode(motors[i].encA, INPUT);
    pinMode(motors[i].encB, INPUT);
    pid[i-4].setParams(1, 0, 0, 128); // Set PID parameters
  }

  attachInterrupt(digitalPinToInterrupt(motors[4].encA), readEncoder<4>, RISING);
  attachInterrupt(digitalPinToInterrupt(motors[5].encA), readEncoder<5>, RISING);

  // Connect to WiFi
  WiFi.begin(ssid, password);
  while (WiFi.status() != WL_CONNECTED) {
    delay(1000);
    Serial.println("Connecting to WiFi...");
  }
  Serial.println("Connected to WiFi");
  Serial.println(WiFi.localIP());

  // Set up web server routes
  server.on("/", handleRoot);
  server.on("/control", HTTP_POST, handleControl);

  // Start the server
  server.begin();
  Serial.println("HTTP server started");
}

void loop() {
  server.handleClient();

   int pos[2];
  noInterrupts();
  for (int i = 4; i < motorCount; i++) {
    pos[i - 4] = posi[i - 4];
  }
  interrupts();

  // Apply PID control to each motor
  for (int i = 4; i < motorCount; i++) {
    int pwr, dir;
    pid[i - 4].evalu(pos[i - 4], target[i], 0.1, pwr, dir); // Updated to include PID control
    setMotorDirection(i, dir == 1);
    setMotorSpeed(i, pwr);
  }

  // for (int i = 0; i < motorCount; i++) {
  //   Serial.print("Motor ");
  //   Serial.print(i);
  //   Serial.print(": Target = ");
  //   Serial.print(target[i]);
  //   Serial.print(", Position = ");
  //   Serial.print(pos[i]);
  //   Serial.print(" ");
  // }
  // Serial.println();
}

void handleRoot() {
  String html = "<html><body>";
  html += "<h1>Motor Control</h1>";
  
  // Master Control for All Motors
  html += "<h2>Master Control</h2>";
  html += "<button onclick=\"control('all_fingers', 'forward')\">All Fingers Forward</button>";
  html += "<button onclick=\"control('all_fingers', 'backward')\">All Fingers Backward</button>";
  html += "<button onclick=\"control('all_fingers', 'stop')\">All Fingers Stop</button>";
  html += "<button onclick=\"control('all_wrists', 'forward')\">All Wrists Forward</button>";
  html += "<button onclick=\"control('all_wrists', 'backward')\">All Wrists Backward</button>";
  html += "<button onclick=\"control('all_wrists', 'stop')\">All Wrists Stop</button>";

  // Individual Motor Control
  html += "<h2>Individual Motor Control</h2>";
  
  for (int i = 0; i < 4; i++) {
    html += "<h3>Finger " + String(i+1) + "</h3>";
    html += "<button onclick=\"control('finger" + String(i+1) + "', 'forward')\">Forward</button>";
    html += "<button onclick=\"control('finger" + String(i+1) + "', 'backward')\">Backward</button>";
    html += "<button onclick=\"control('finger" + String(i+1) + "', 'stop')\">Stop</button>";
  }
  
  for (int i = 0; i < 2; i++) {
    html += "<h3>Wrist " + String(i+1) + "</h3>";
    html += "<button onclick=\"control('wrist" + String(i+1) + "', 'forward')\">Forward</button>";
    html += "<button onclick=\"control('wrist" + String(i+1) + "', 'backward')\">Backward</button>";
    html += "<button onclick=\"control('wrist" + String(i+1) + "', 'stop')\">Stop</button>";
  }

  // Special Controls
  html += "<h2>Special Controls</h2>";
  html += "<button onclick=\"control('pitch', '')\">Pitch</button>";
  html += "<button onclick=\"control('pitch_counter', '')\">Pitch Counter</button>";

  html += "<script>";
  html += "function control(motor, action) {";
  html += "  fetch('/control', {";
  html += "    method: 'POST',";
  html += "    headers: {'Content-Type': 'application/x-www-form-urlencoded'},";
  html += "    body: 'motor=' + motor + '&action=' + action";
  html += "  }).then(response => response.text()).then(data => console.log(data));";
  html += "}";
  html += "</script>";
  
  html += "</body></html>";
  server.send(200, "text/html", html);
}


void handleControl() {
  String motorStr = server.arg("motor");
  String action = server.arg("action");

  if (motorStr == "all") {
    for (int i = 0; i < motorCount; i++) {
      controlMotor(i, action);
    }
    server.send(200, "text/plain", "OK");
  } else if (motorStr == "pitch") {
    target[0] += 300;  // First motor target increases by 300
    target[1] -= 300;  // Second motor target decreases by 300
    server.send(200, "text/plain", "Pitch set");
  } else if (motorStr == "pitch_counter") {
    target[0] -= 300;  // First motor target decreases by 300
    target[1] += 300;  // Second motor target increases by 300
    server.send(200, "text/plain", "Pitch Counter set");
  } else {
    int motor = motorStr.toInt();
    if (motor >= 0 && motor < motorCount) {
      controlMotor(motor, action);
      server.send(200, "text/plain", "OK");
    } else {
      server.send(400, "text/plain", "Invalid motor");
    }
  }
}


void controlMotor(int motor, String action) {
  if (action == "forward") {
    target[motor] += 200; // Increase target by 200 encoder counts for forward movement
  } else if (action == "backward") {
    target[motor] -= 200; // Decrease target by 200 encoder counts for backward movement
  } else if (action == "stop") {
    target[motor] = posi[motor]; // Stop at current position
  }
}

void setMotorDirection(int motor, bool forward) {
  if (motors[motor].isDualDir) {
    if (forward) {
      ss.digitalWrite(motors[motor].dir1, HIGH);
      ss.digitalWrite(motors[motor].dir2, LOW);
    } else {
      ss.digitalWrite(motors[motor].dir1, LOW);
      ss.digitalWrite(motors[motor].dir2, HIGH);
    }
  } else {
    bool actualDirection = motors[motor].reversed ? !forward : forward;
    ss.digitalWrite(motors[motor].dir1, actualDirection ? HIGH : LOW);
  }
}

void setMotorSpeed(int motor, int speed) {
  if (motors[motor].isPwmSeesaw) {
    ss.analogWrite(motors[motor].pwm, map(speed, 0, 255, 0, 65535), 16);
  } 
  else {
    analogWrite(motors[motor].pwm, speed);
  }
}

template <int j>
void readEncoder() {
  int b = digitalRead(motors[j].encB);
  if (b > 0) {
    posi[j]++;
  } else {
    posi[j]--;
  }
}

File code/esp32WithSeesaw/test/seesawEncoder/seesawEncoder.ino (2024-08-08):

#include "Adafruit_seesaw.h"

Adafruit_seesaw ss;

#define ENCA 4 
#define ENCB 16
#define PWM 15
#define DIR_PIN 8  // This will be controlled by the seesaw

volatile int posi = 0;
long prevT = 0;
float eprev = 0;
float eintegral = 0;

void setup() {
  Serial.begin(9600);
  
  while (!Serial) delay(10);   // wait until serial port is opened
  
  if(!ss.begin()){
    Serial.println("seesaw not found!");
    while(1) delay(10);
  }
  
  Serial.println(F("seesaw started OK!"));

  ss.pinMode(DIR_PIN, OUTPUT);

  pinMode(ENCA, INPUT);
  pinMode(ENCB, INPUT);
  attachInterrupt(digitalPinToInterrupt(ENCA), readEncoder, RISING);
  
  pinMode(PWM, OUTPUT);
  
  Serial.println("target pos");
}

void loop() {
  // set target position
  Serial.print(10000); 
  Serial.print(", ");
  Serial.print(-10000);
  Serial.print(", ");
  int target = 1525;

  // PID constants
  float kp = 1.0;
  float kd = 0.1;
  float ki = 0.01;

  // time difference
  long currT = micros();
  float deltaT = ((float) (currT - prevT)) / (1.0e6);
  prevT = currT;

  // Read the position
  int pos = 0; 
  noInterrupts(); // disable interrupts temporarily while reading
  pos = posi;
  interrupts(); // turn interrupts back on
  
  // error
  int e = target - pos;

  // derivative
  float dedt = (e-eprev) / (deltaT);

  // integral
  eintegral = eintegral + e * deltaT;

  // control signal
  float u = kp * e + kd * dedt + ki * eintegral;

  // motor power
  float pwr = fabs(u);
  if (pwr > 127) {
    pwr = 127;
  }

  // motor direction
  int dir = 1;
  if (u < 0) {
    dir = -1;
  }

  // signal the motor
  setMotor(dir, pwr, PWM, DIR_PIN);

  // store previous error
  eprev = e;

  Serial.print(target);
  Serial.print(", ");
  Serial.print(pos);
  Serial.println();
}

void setMotor(int dir, int pwmVal, int pwm, int dirPin) {
  analogWrite(pwm, pwmVal);
  if (dir == 1) {
    ss.digitalWrite(dirPin, HIGH);
  }
  else if (dir == -1) {
    ss.digitalWrite(dirPin, LOW);
  }
  else {
    // For stop condition, set PWM to 0
    analogWrite(pwm, 0);
  }  
}

void readEncoder() {
  int b = digitalRead(ENCB);
  if (b > 0) {
    posi++;
  }
  else {
    posi--;
  }
}

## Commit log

2024-07-08 add(code/arduino): pid tuning
2024-07-13 add(electrical): bionicBoard design
    [bionic.kicad_pcb, bionic.kicad_sch]
2024-07-13 add(electrical/symbol): Updated Components
    [bionic.kicad_sch]
2024-07-14 update(electrical): bionicBoard 'ERC Passed!'
    [bionic.kicad_sch]
2024-07-16 add(electrical/footprint): Updated Footprints
    [bionic.kicad_pcb, bionic.kicad_sch]
2024-07-16 update(electrical): All Footprint Assigned!
    [bionic.kicad_pcb, bionic.kicad_sch]
2024-07-16 update(electrical/pcb): signal wiring Complete!!
    [bionic.kicad_pcb, bionic.kicad_sch]
2024-07-17 update(electrical/pcb): DRC Passed! and Updated 3D-Models
    [CD4069.step, JST_XH_1x03_P2.54mm_Vertical.step, JST_XH_1x06_P2.54mm_Vertical.stp, LM338T.step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]
2024-07-17 update(electrical/pcb): Updated Placement and Reduce Board
    [LED_RGB_H1mm.stp, bionic.kicad_pcb, bionic.kicad_sch]
2024-07-18 update(electrical/pcb): Finialized v1.0 Design
    [bionic.kicad_pcb, bionic.kicad_sch]
2024-07-21 add(code): esp32 ui & motorpid code
2024-07-21 add(data): sensor data acquisition and processing
    [curl2.xlsx, indexMidlle.xlsx, ringLittle.xlsx, roll.xlsx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]
2024-07-27 refactor(structure): rename and reorganize folders and files
    [Assem2 - Bevel Gear3-1.STL, Assem2 - Bevel Gear3-3.STL, Assem2 - Bevel Gear3-4.STL, Assem2 - Part17-1.STL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]
2024-07-31 add(code/opencv): Add scripts for grasping and finger control
2024-08-08 add(code): test codes using esp32 with seesaw
2024-08-08 add(code): Build code for Bionic Arm with ESP32 and Seesaw integration
